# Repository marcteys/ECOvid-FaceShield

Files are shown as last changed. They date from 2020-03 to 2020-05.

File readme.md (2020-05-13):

# ECOvid Protective Face Sheild

A protective face shield fast to print and that use a minimum amount of material. 

The face shield prints in **20 minutes** and uses only **2.35m** of filament.

This face shield is currently used in ICU MIR  at Hospital Cochin (APHP, Paris).  This design is validated by the Hygiene Committee of the hospital. 

You can read a thread on the design process, the tools used and the reasons for another design here on Twitter: https://twitter.com/marcteyssier/status/1245010785744683009

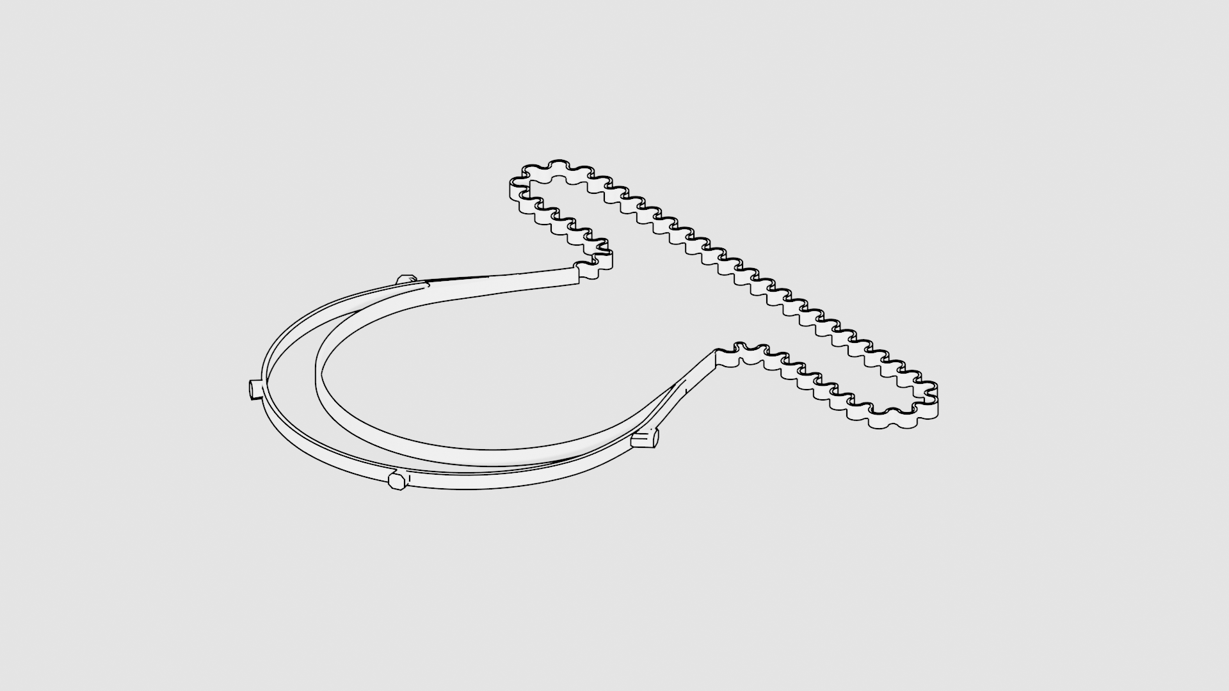
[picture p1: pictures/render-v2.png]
Render


## Print Settings

The *.curaprofile* is present on this repo, as well as some *.3mf* files. The profile can be imported on `Preferences>Configure Cura>Profiles>Import`. 

Here are the important settings with a 0.4 nozzle. 
- Layer height: *0.38mm*
- Initial layer height: *0.28mm*
- Line width: *0.46mm* 
- Fill gaps between walls: *Nowhere*
- Infill density *80%*
- Print speed: *90 mm/s*
- Initial layer speed: *25 mm/s*
- Generate support: *No*
- Build plate adhesion Type: *Skirt*

**Note:** It is important that there is no holes between the layers and the walls. Adujst your printer settings if you see that there is a hole between two walls: Change the setting *Fill gaps between walls*  to * Everywhere* if it's the case.

## Fabrication

### Material
- A4 transparent sheet 
- Standard EU punch hole, 2 holes ([exemple](https://www.google.com/search?q=punch+hole+2&hl=en&sxsrf=ALeKk01VRlmL0uM0lpgbsiWLHW1cRw-DiQ:1585672351383&source=lnms&tbm=isch&sa=X&ved=2ahUKEwjr1-_pkcXoAhXU8OAKHVQoCY4Q_AUoAXoECAsQAw))
- 3d printed 

### Steps
- 3D print the face shield 
- Setup your hole puncher to A6 settings
- Punch two holes on one side of the transparent shield, flip it over and punch two more holes from the other side. 
- Attach the transparent sheet
- Sterilize

## Edit the model

The source (*.blend*) is included. It is composed of three separate parts, **External**, **Internal** and **Strap**. I rely on non-destructive modelling techniques and used a lot of boolean operations.

To adjust the height of the stack, select each part and edit the value *count* of the *Array* modifier. 

To export the model, select the 3 parts and click *Export* on the 3D-print panel.

The following add-ons were used: Measure-it, 3D-Print Toolbox,  Bool Tool, Curve Tools and Bezier Utilities. Freestyle for rendering. 

## Credits 

This face shield is a remix the one proposed by [Qualup](http://www.spiderbot.eu/covid-19-ecran-facial-imprime-sterilisable/)

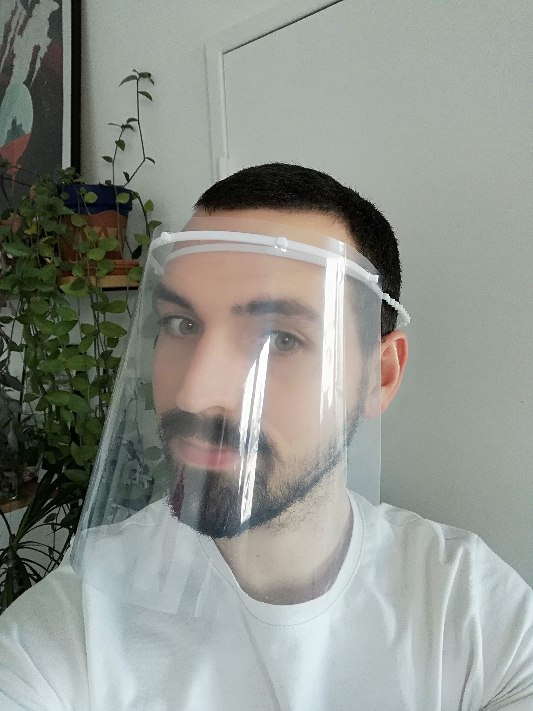
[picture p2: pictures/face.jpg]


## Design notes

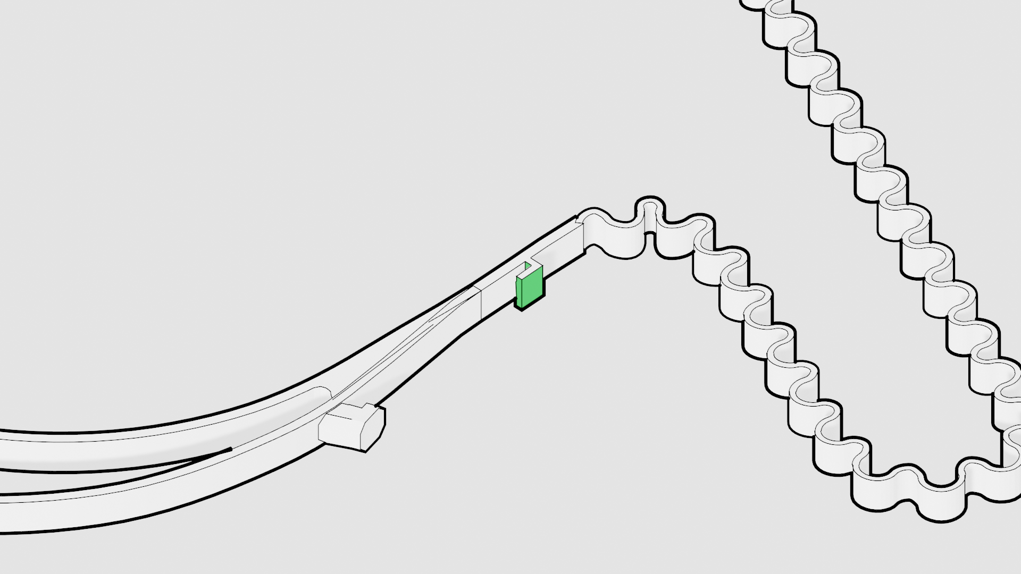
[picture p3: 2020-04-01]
pictures/sheet.png

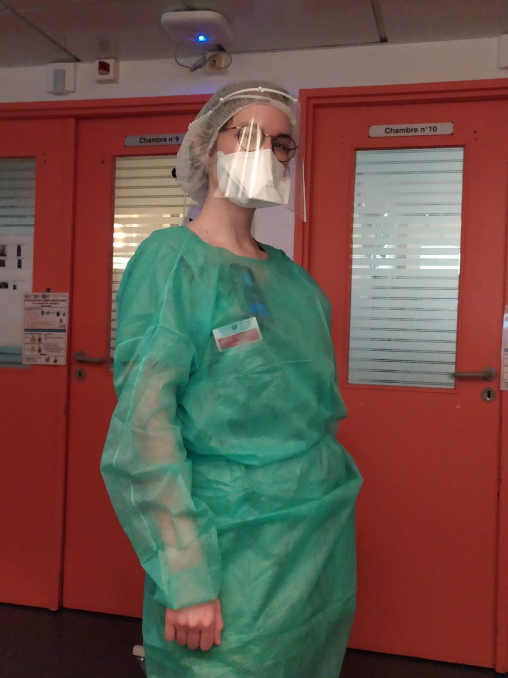
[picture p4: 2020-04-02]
pictures/nurse.jpeg

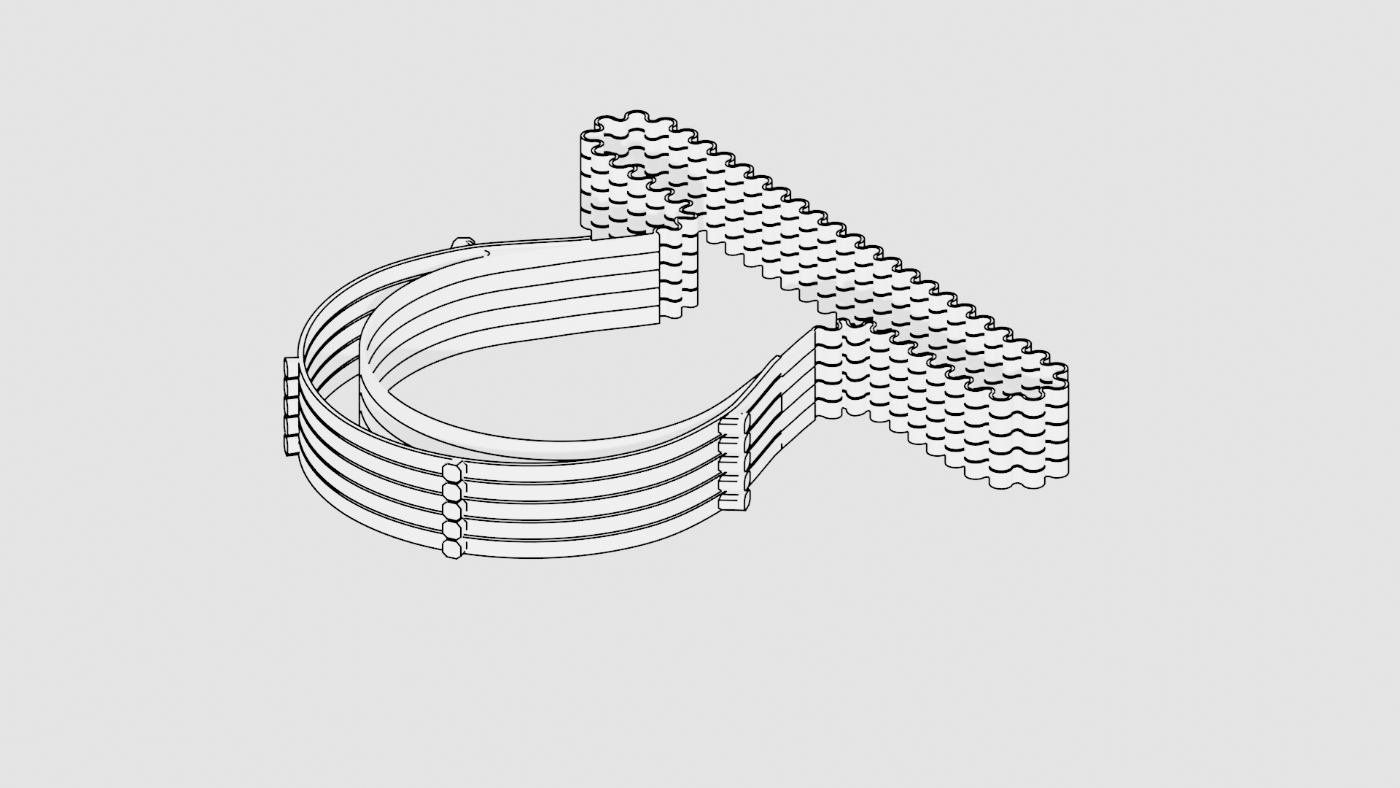
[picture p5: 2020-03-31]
pictures/render-stack.png

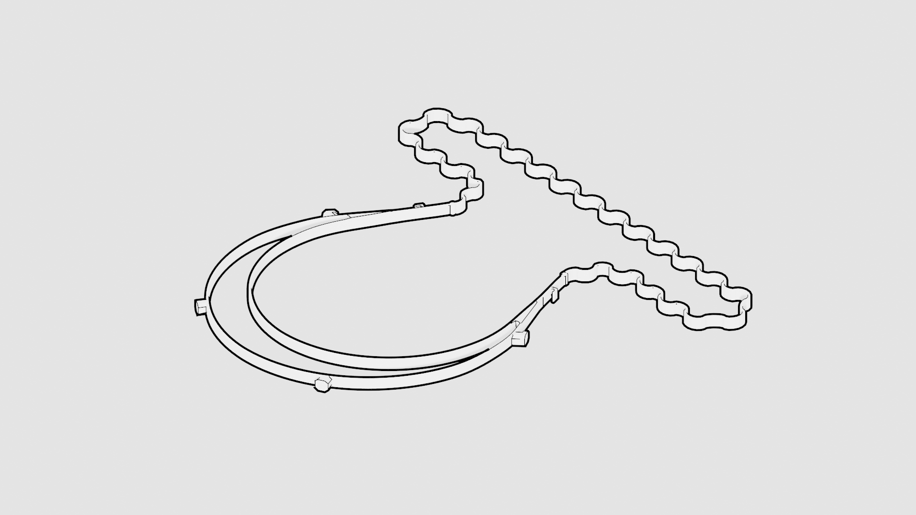
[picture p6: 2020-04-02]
pictures/render-v3.png

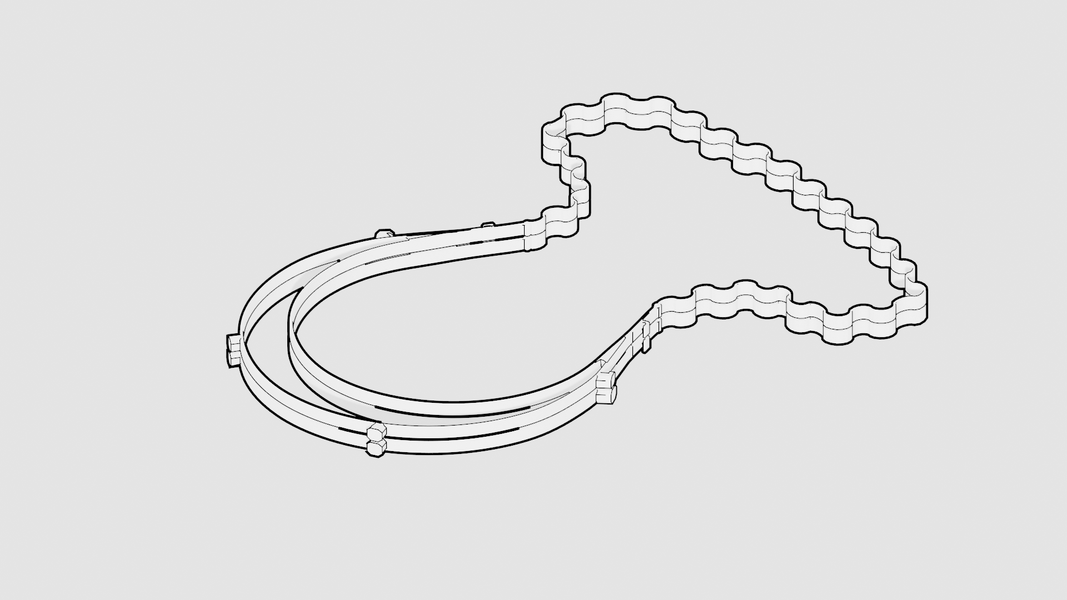
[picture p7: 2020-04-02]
pictures/render-v4.png

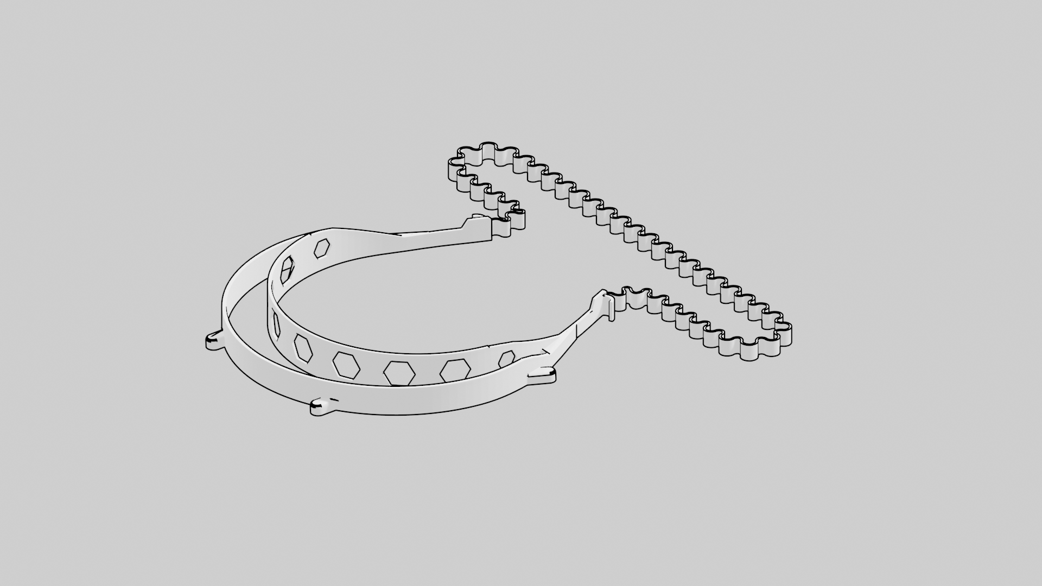
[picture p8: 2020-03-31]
pictures/render-v1.png

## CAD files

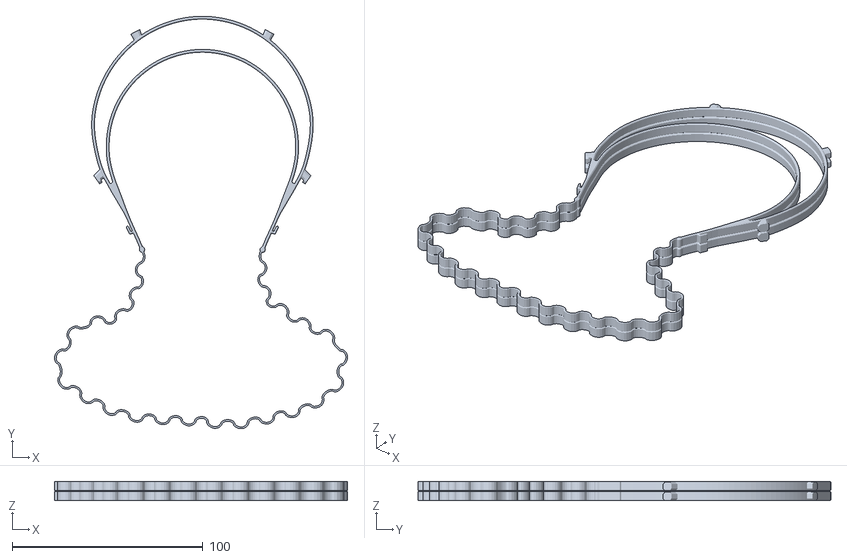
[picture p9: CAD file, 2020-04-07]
ecovid-faceshield-stack-2.stl
153.8 x 216.5 x 10.1

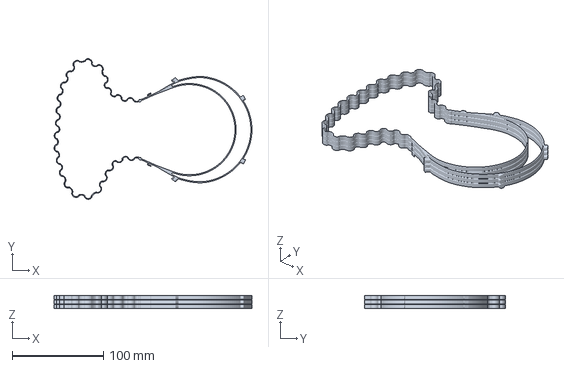
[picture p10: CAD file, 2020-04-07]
ecovid-faceshield.3mf
216.5 x 153.8 x 14.5 mm

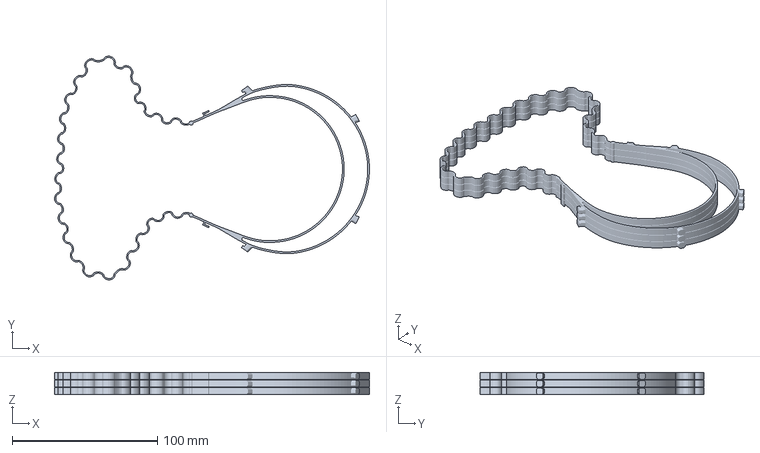
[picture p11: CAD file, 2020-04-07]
CE3_ecovid-faceshield-stack-3.3mf
216.5 x 153.8 x 15.4 mm

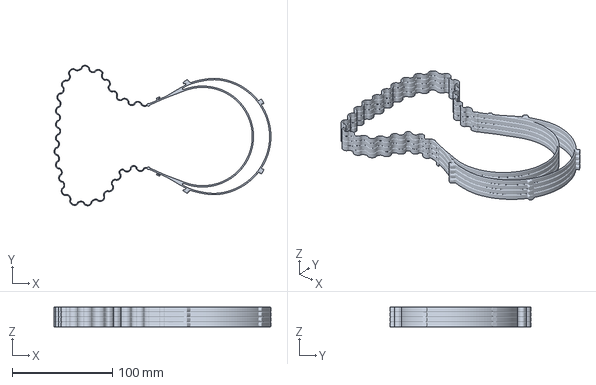
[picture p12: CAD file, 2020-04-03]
ecovid-faceshield-small-4.3mf
216.8 x 140.5 x 19.8 mm

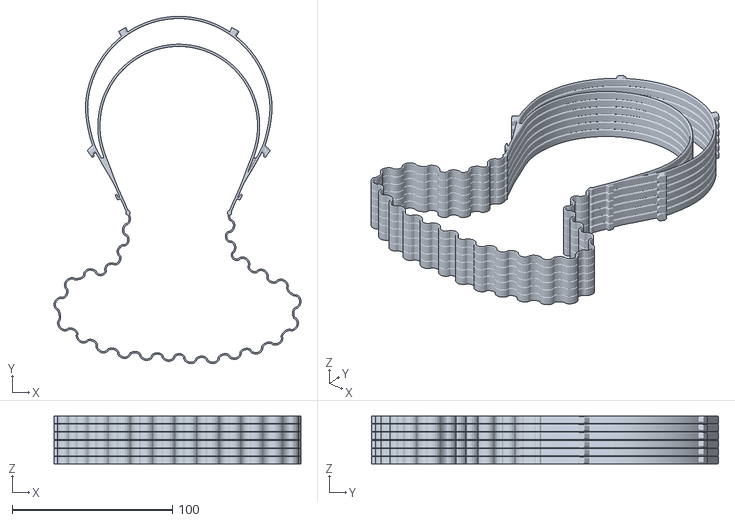
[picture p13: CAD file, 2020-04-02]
ecovid-faceshield-stack-6.stl
153.9 x 216.5 x 29.9

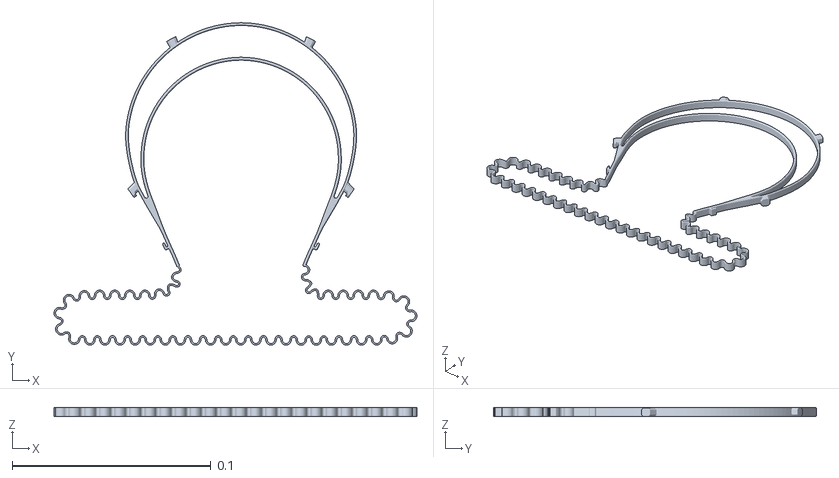
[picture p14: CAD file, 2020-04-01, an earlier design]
old_version/ecovid-faceshield-v10.stl
0.183 x 0.162 x 0.00473

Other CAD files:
ecovid-faceshield-stack-3.stl
ecovid-faceshield-stack-2_small.stl
ecovid-faceshield.stl

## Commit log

2020-03-31 initial commit with v10
    [ecovid-faceshield-v10.3mf, ecovid-faceshield-v10.stl]
2020-03-31 adjusting position of from spacer, adding lateral holder
    [ecovid-faceshield-v10-stack.stl]
2020-03-31 fix layer height as a multiple of 0.3
    [ecovid-faceshield-v10.blend]
2020-03-31 fix array offset as multiple of 0.3 (5.1, 4.8 + 0.3)
    [ecovid-faceshield-v10.blend]
2020-03-31 Add a link to Marc's twitter thread
    The thread is clear, explain the reasons for the design, shows that the end-users have been involved in the design, etc. so it's an useful reference for people that might find the repo.
2020-04-01 fixing sizes settings
    [ecovid-faceshield-v10-stack.stl, ecovid-faceshield-v10.3mf, ecovid-faceshield-v10.blend, ecovid-faceshield-v10.stl]
2020-04-01 fix wrong scale of stl
    [ecovid-faceshield-v10.blend, ecovid-faceshield-v10.stl]
2020-04-01 fixing the side lock and adding stack 6 settings
    [ecovid-faceshield-v10.blend]
2020-04-01 moving slightly the back punch hole
    [ecovid-faceshield-v10.blend]
2020-04-01 fixing back spacer
    [ecovid-faceshield-v10.blend, ecovid-faceshield-v10.stl]
2020-04-01 more optimization for fast print
    [ecovid-faceshield-v10.blend, ecovid-faceshield-v10.stl]
2020-04-01 new version, faster print settings
    [ecovid-faceshield-v10.3mf, ecovid-faceshield-v10.blend, ecovid-faceshield-v10.stl, ecovid-faceshield-v11.blend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]
2020-04-02 updating the design
    [ecovid-faceshield-stack-3.stl, ecovid-faceshield-stack-6.stl, ecovid-faceshield-stack-62.stl, ecovid-faceshield-v11.blend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]
2020-04-02 updating to latests models
    [ecovid-faceshield-stack-3.stl, ecovid-faceshield-stack-6.stl, ecovid-faceshield-stack-62.stl, ecovid-faceshield-v11.blend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]
2020-04-03 new models
    [ecovid-faceshield-small-4.3mf, ecovid-faceshield-stack-2_small.stl, ecovid-faceshield-stack-3.stl, ecovid-faceshield-v11-small.blend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]
2020-04-07 last updates
    [CE3_ecovid-faceshield-stack-3.3mf, ecovid-faceshield-stack-2.stl, ecovid-faceshield-stack-3.stl, ecovid-faceshield-v11.blend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]
